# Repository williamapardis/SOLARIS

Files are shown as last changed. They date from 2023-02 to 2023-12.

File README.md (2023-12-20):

# SOLARIS
The Submersible Oceanic Luminescent Analyzer of Reactive Intermediate Species (SOLARIS) is a developmental instrument designed to make measurements in the ocean of a fleetingly scarce compound called superoxide(O<sup>2-</sup>), a reactive oxygen species(ROS) and made the first measurements of this chemical in the deep sea. SOLARIS utilizes the properties of chemiluminescence, a chemical reaction that produces light. Analysis involves mixing a chemical reagent with the seawater to be analyzed, after which a reaction occurs and produces light proportional to the level of superoxide. Measuring this light with a highly sensitive optical detector, a photon counting photomultiplier tube(PMT), we can very precisely determine how much superoxide is in the environment. Peristaltic pumps dispense reagents and seawater, which are encased in housings filled with (incompressible) oil to protect them from the corrosive environment. Electronics are encased in hermetically sealed pressure vessels held at atmospheric pressure  to protect them from both the seawater and hydrostatic pressure, allowing operation to depths of up to 4500 meters, corresponding to pressures of greater than 400 atmospheres.
SOALRIS has also been adapted to measure hydrogen peroxide (H<sub>2</sub>O<sub>2</sub>) and made some of the first ever measurments of this ROS species in the deep sea.
<div class="center">
  <table>
    <tr>
      <td>SOLARIS Pressure Testing</td>
       <td>System Schematic</td>
    </tr>
    <tr>
      <td></td>
      <td></td>
    </tr>
  </table>
</div>
  
## Hardware
SOLARIS is a complex assembly of mechanical electrical and fluidic components.

### Mechanical
The mechanical assembly of SOLARIS is broken into two sub-assemblies we reffer to as the Analyzer Assembly and the Reagent Assembly. 

#### Analyzer Assembly
The analyzer assembly is designed to be minipulated by a under water vehicle to be positioned near the area of interest to be analyzed.
<table>
  <tr>
    <td>Drawing</td>
    <td>On Deck</td>
    <td>In Water</td>
  </tr>
  <tr>
    <td></td>
    <td></td>
    <td></td>
  </tr>
</table>
<table>
  <tr>
    <td>Flow Cell</td>
  </tr>
  <tr>
    <td></td>
    <td>The Seawater sample and the chemiluminecent reagent (MCLA for measurement of O<sup>2-</sup>) enter the center of the spiral flow cell from their respective ports. This cell is optically monitoured through a optically clear saphire window by the PMT. Mixed fluids outflow the bottom port and are exhausted.</td>
  </tr>
</table>

#### Reagent Assembly
<table>
  <tr>
    <td>Drawning</td>
    <td>Diagram</td>
    <td>Image</td>
  </tr>
  <tr>
    <td></td>
    <td></td>
    <td>The Reagent assembly</td>
  </tr>
</table>

### Electrical
SOLARIS ELECTRICAL OVERVIEW:
- Pumps are driven by 7 Allmotion motor controllers.
- Allmotion motor controllers are controlled by custon WHOI PCB 23-0001-01.  Power to them is directly from instrument input.
- WHOI PCB 23-0001-01 contains Adafruit ItsyBitsy M4 which controlls the motor drivers over serial and manages overall device comminicaiton.  This board also prives power and communication to the PMT.
- COTS temperature controller (Wavelength Electronics) controlls SOTS chamber temperature.
- All data is stored onbaord the "topside" computer (none onboard Solaris itself).

#### Main Electrical Housing (Reagent Assembly)
<table>
  <tr>
    <td>Electronics Chassis</td>
    <td>Electronics Chassis Side</td>
    <td>Electronics Chassis Bottom</td>
  </tr>
  <tr>
    <td></td>
    <td></td>
    <td></td>
  </tr>
</table>

#### PMT Electrical Housing (Analyzer Assembly)
<table>
  <tr>
    <td>Full View PCB</td>
     <td>Zoomed View</td>
  </tr>
  <tr>
    <td></td>
    <td></td>
  </tr>
</table>

#### 23-0001-01 Custom Printed Circuit Board
<table>
  <tr>
    <td>Front PCB</td>
     <td>Bottom PCB</td>
  </tr>
  <tr>
    <td></td>
    <td></td>
  </tr>
</table>

#### Motors Controllers
The 7 pumps on SOLARIS are driven by motors and controled with [All Motion](https://www.allmotion.com/) [EZ10EN stepper motor driver](https://www.allmotion.com/ez10en). The 7 motor controllers share a parallel RS485 serial bus and are comunicated with a serial port on the 23-0001 controller through a [RS323 to RS485 converter](https://www.allmotion.com/rs485-ne).

#### Temperature Controller
The SOTs temperature control uses a Wavelength Electronics [RHM5K-CH termprature controller](https://www.teamwavelength.com/product/rhm5k-ch-5-a-unipolar-chassis-mt-temp-controller/) in combination with a resistive heater and thermistor. In order to maintain temperature stability we decided to remove the the integration capacitor.

#### Cables
[tubing](https://www.mcmaster.com/5549K55/) used with [MCPBOF](https://www.macartney.com/what-we-offer/systems-and-products/connectors/subconn/subconn-micro-circular-series/subconn-micro-circular-2-3-4-5-6-and-8-contacts-and-g2-2-3-and-4-contacts/)

### Fluid Handling

#### Pump Heads
<table>
  <tr>
    <td>Pump Head</td>
  </tr>
  <tr>
    <td></td>
    <td>The [100CPT parastaltic pump heads](https://www.wmcpumps.com/100cpt-series-micro-peristaltic-pump) were purchased from Williamson Manufacturing Company and used with the [100 Series Tube Sets](https://www.wmcpumps.com/100200220-series-tube-sets).</td>
  </tr>
</table>

#### Motors
These pumpheads are driven with the [HT11-021-G022 motor/gearbox](https://github.com/williamapardis/SOLARIS/blob/main/hardware/electrical/datasheets/Motor/HT11_021_GXXX_RevA_GEARMOTOR_ASSY-3079755.pdf) combo from Applied Motion Products. The output of the gearbox is coupled to the pump head with a custom machined shaft.



#### [tubing](https://www.mcmaster.com/5384K515/)

## Software
SOFTWARE OVERVIEW:
- There is a Matlab GUI that runs SOLARIS.  The GUI mostly updates pump speeds and and plots and stores data.
- There is firmware on the ItsyBitsy that sets the initial PMT and motor controller settings.  It also transmits data from the PMT to the topside computer, and it transmits speeds from the topside computer to the motor controllers. 

### The Application

#### Start up page


#### Real-Time GUI


#### Autonomous Mission Planning

### Using the Emulator

Download & install the free serial port emulator (emulator\free-virtual-serial-port-tools.exe)
  Select creat local bridge & configure:
    First port name: COM1
    Secound port name: COM2
  Create - select "Creat non-permanent device" checkbox and then OK
Run the emulator
  '''python3 emulator.py'''
Select previous datafile using explorer
Open the app and use on COM2

#### Dependencies
'''pip3 install scipy'''

### Firmware

#### 23_0001_01_Rb

#### Passthrough

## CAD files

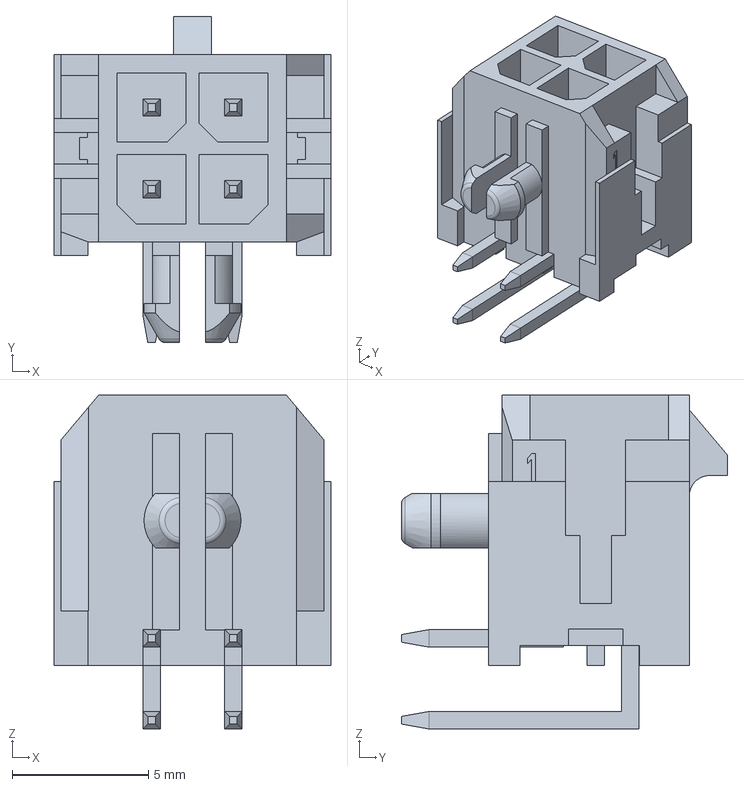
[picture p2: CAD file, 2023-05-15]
hardware/electrical/PCBs/23-0001/imported/3d/2_2 molex.stp
10.2 x 11.9 x 12.2 mm

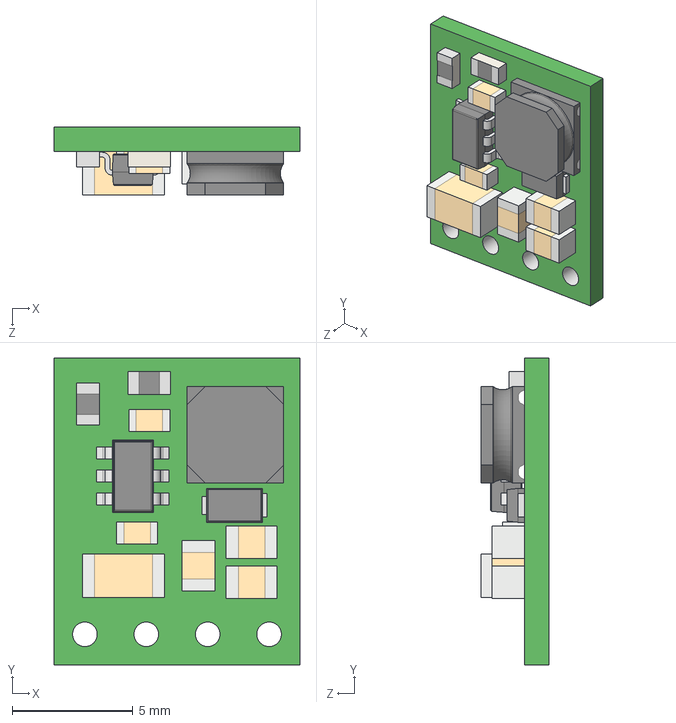
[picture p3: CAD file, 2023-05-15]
hardware/electrical/PCBs/23-0001/imported/3d/step-down-voltage-regulator-d24v3fx-d24v6fx-d36v6fx.step
10.2 x 12.7 x 2.82 mm

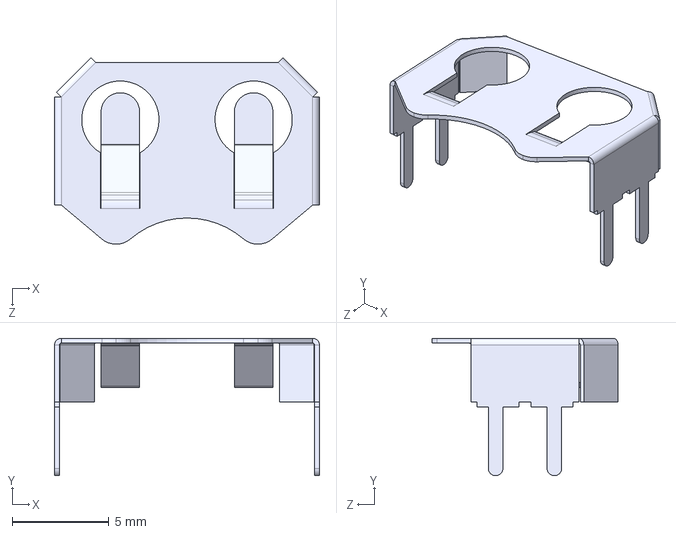
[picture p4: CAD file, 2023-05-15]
hardware/electrical/PCBs/23-0001/imported/3d/BK-917.STEP
13.7 x 7.11 x 9.65 mm

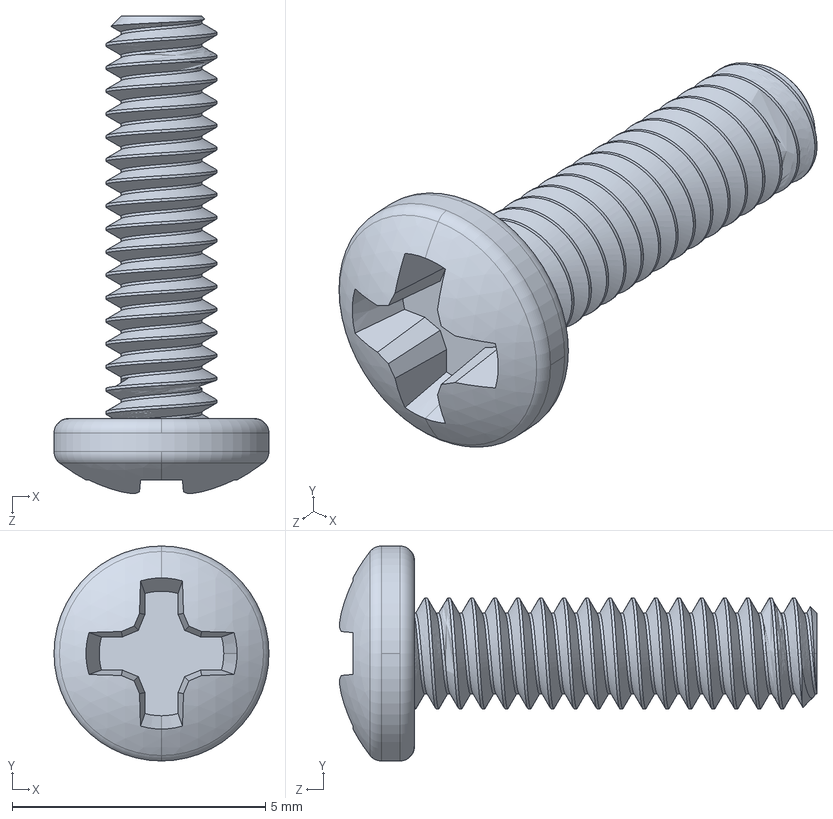
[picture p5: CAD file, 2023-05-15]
hardware/electrical/PCBs/23-0001/imported/3d/91400A056_MIL SPEC PAN HEAD PHILLIPS MACHINE SCREW.STEP
4.24 x 4.24 x 9.42 mm

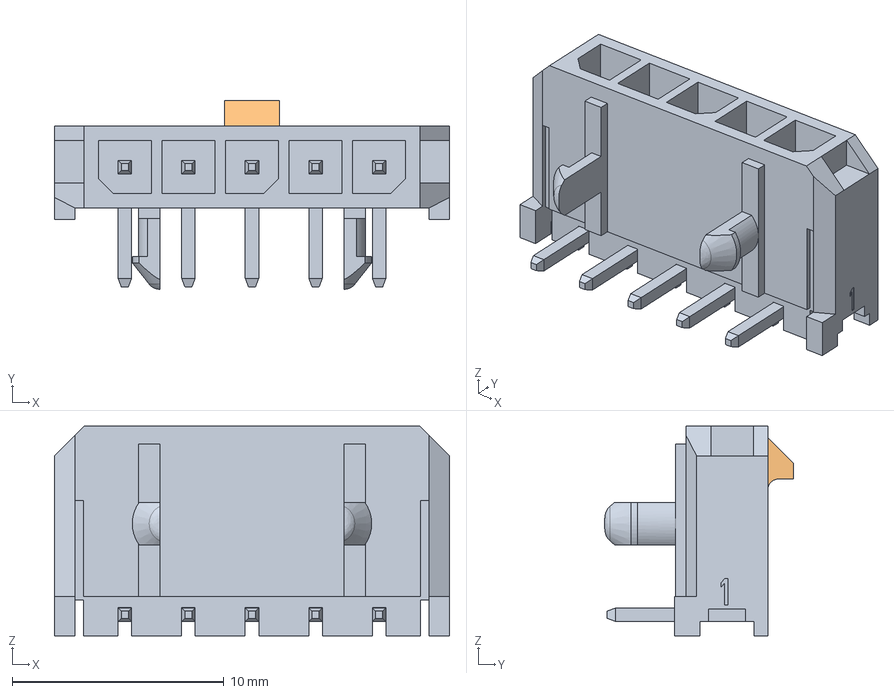
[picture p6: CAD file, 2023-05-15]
hardware/electrical/PCBs/23-0001/imported/3d/436500500.stp
18.6 x 8.91 x 9.90 mm

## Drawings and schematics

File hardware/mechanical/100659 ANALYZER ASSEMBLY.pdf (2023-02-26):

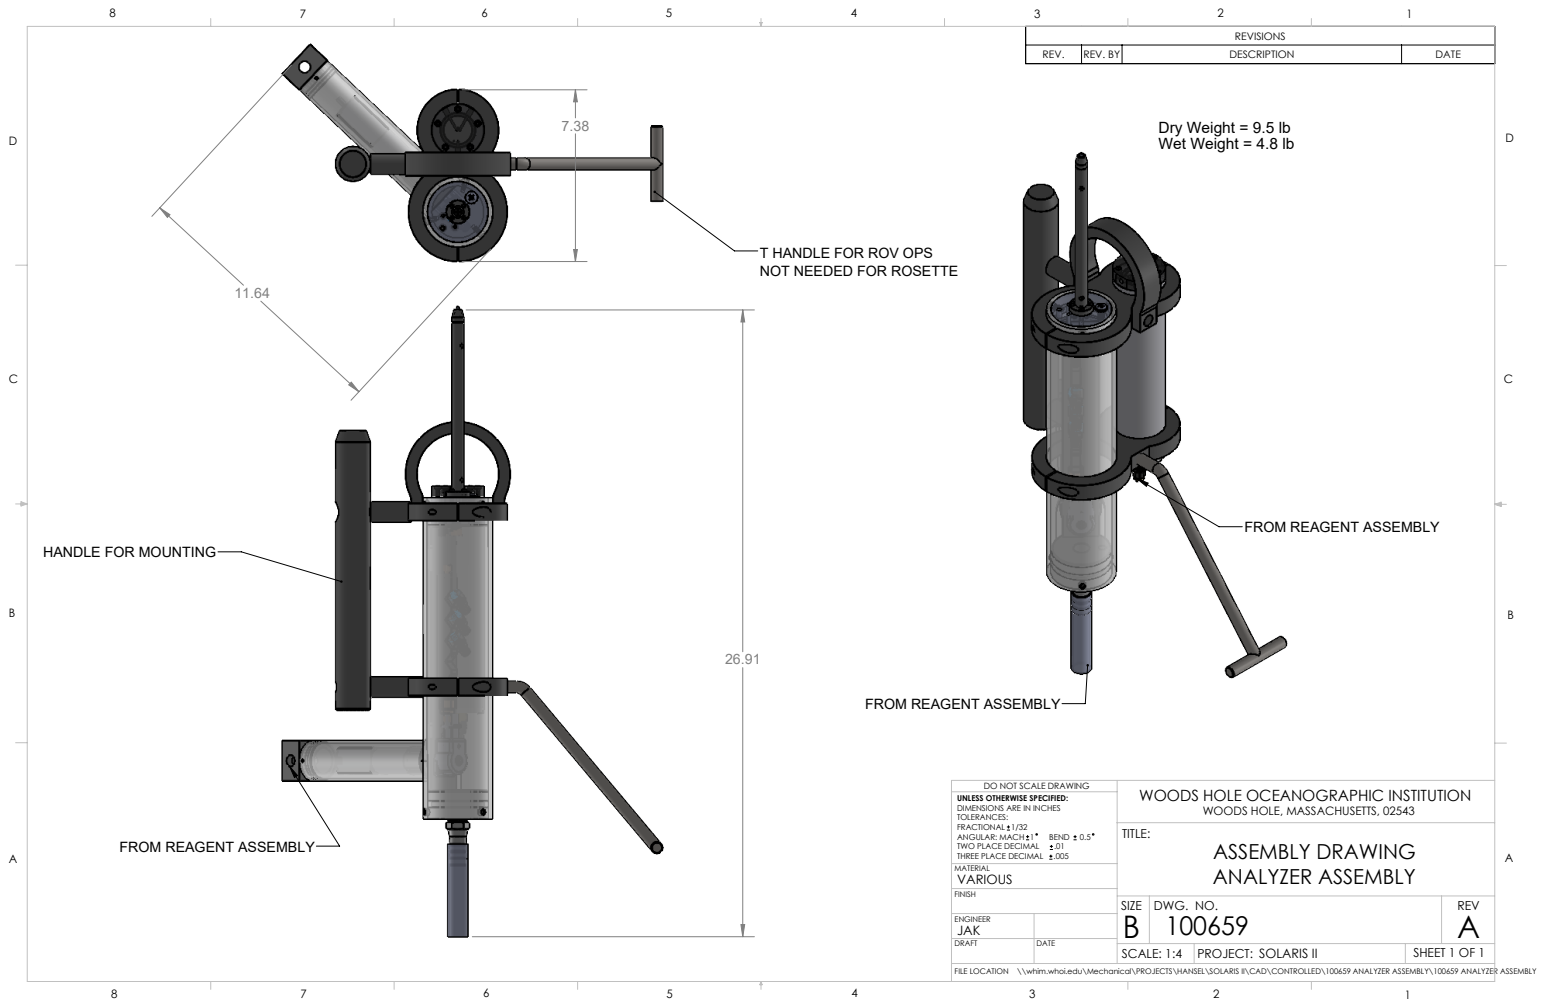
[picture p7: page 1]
REV.; REV. BY; DESCRIPTION; DATE; ANGULAR: MACH 1; BEND 0.5; TWO PLACE DECIMAL; DWG. NO.; REV; SHEET 1 OF 1; SCALE: 1:4; B ENGINEER; VARIOUS; ANALYZER ASSEMBLY

Dry Weight = 9.5 lb
Wet Weight = 4.8 lb

T HANDLE FOR ROV OPS
NOT NEEDED FOR ROSETTE

FROM REAGENT ASSEMBLY

HANDLE FOR MOUNTING

DO NOT SCALE DRAWING
UNLESS OTHERWISE SPECIFIED:
DIMENSIONS ARE IN INCHES
TOLERANCES:
FRACTIONAL 1/32
THREE PLACE DECIMAL .005
MATERIAL

WOODS HOLE OCEANOGRAPHIC INSTITUTION
ASSEMBLY DRAWING

WOODS HOLE, MASSACHUSETTS, 02543

PROJECT: SOLARIS II

FILE LOCATION \\whim.whoi.edu\Mechanical\PROJECTS\HANSEL\SOLARIS II\CAD\CONTROLLED\100659 ANALYZER ASSEMBLY\100659 ANALYZER ASSEMBLY

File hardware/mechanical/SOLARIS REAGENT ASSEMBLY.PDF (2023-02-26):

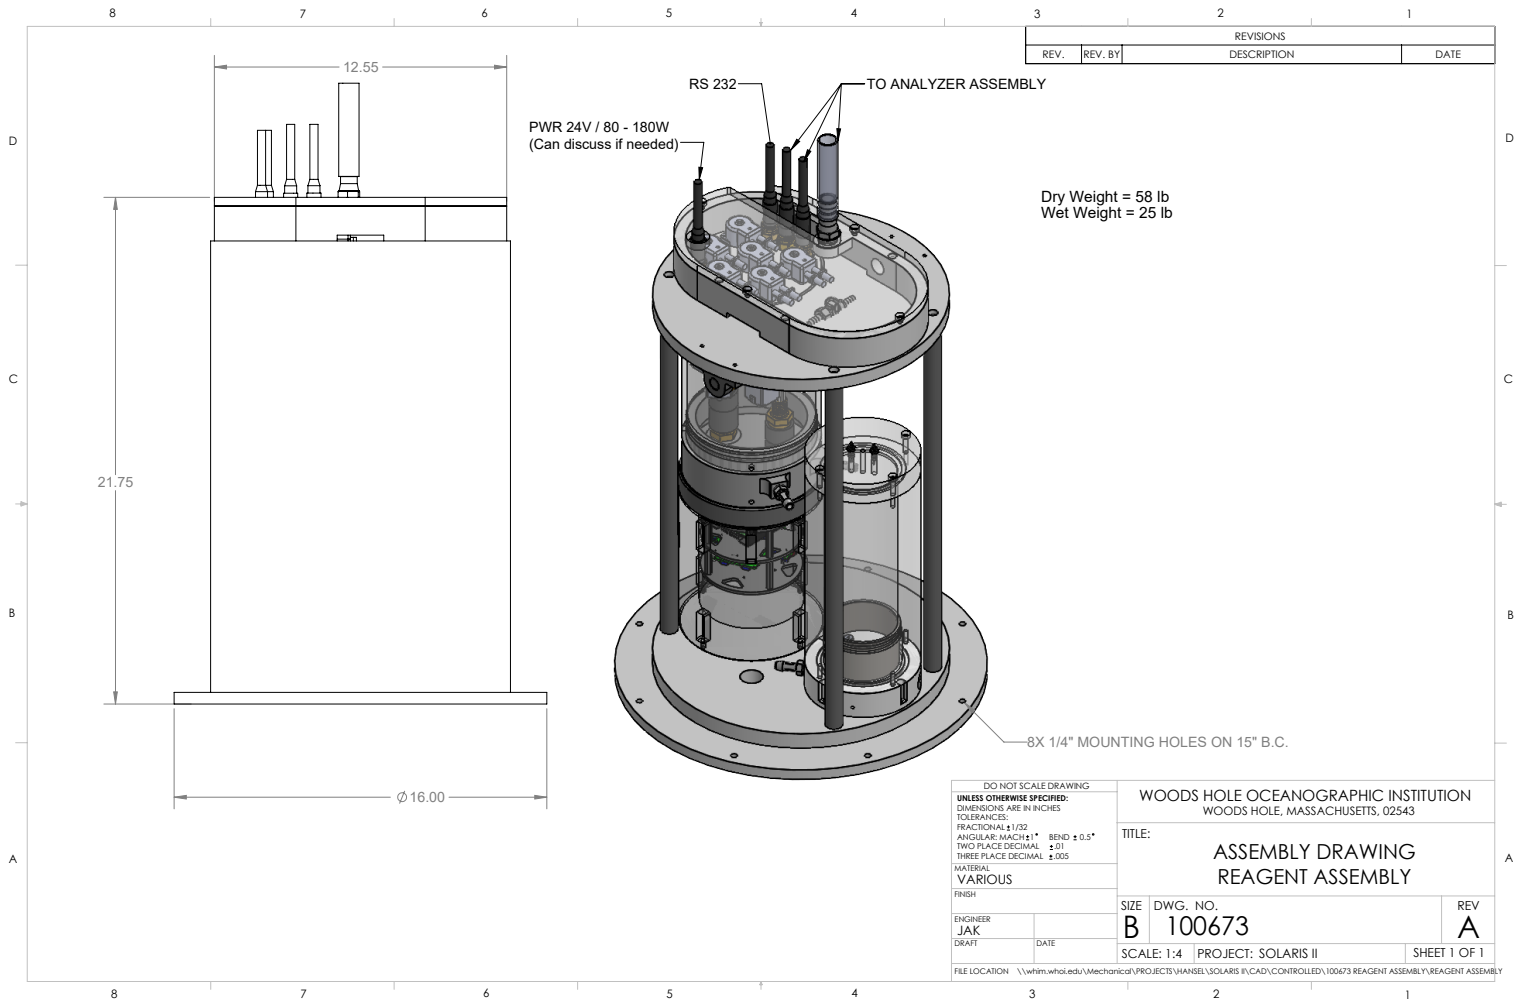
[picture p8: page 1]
REV.; REV. BY; DESCRIPTION; DATE; ANGULAR: MACH 1; BEND 0.5; TWO PLACE DECIMAL; DWG. NO.; REV; SHEET 1 OF 1; SCALE: 1:4; B ENGINEER; VARIOUS; REAGENT ASSEMBLY

TO ANALYZER ASSEMBLY

PWR 24V / 80 - 180W
(Can discuss if needed)

Dry Weight = 58 lb
Wet Weight = 25 lb

8X 1/4" MOUNTING HOLES ON 15" B.C.

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

WOODS HOLE OCEANOGRAPHIC INSTITUTION
ASSEMBLY DRAWING

WOODS HOLE, MASSACHUSETTS, 02543

PROJECT: SOLARIS II

FILE LOCATION \\whim.whoi.edu\Mechanical\PROJECTS\HANSEL\SOLARIS II\CAD\CONTROLLED\100673 REAGENT ASSEMBLY\REAGENT ASSEMBLY

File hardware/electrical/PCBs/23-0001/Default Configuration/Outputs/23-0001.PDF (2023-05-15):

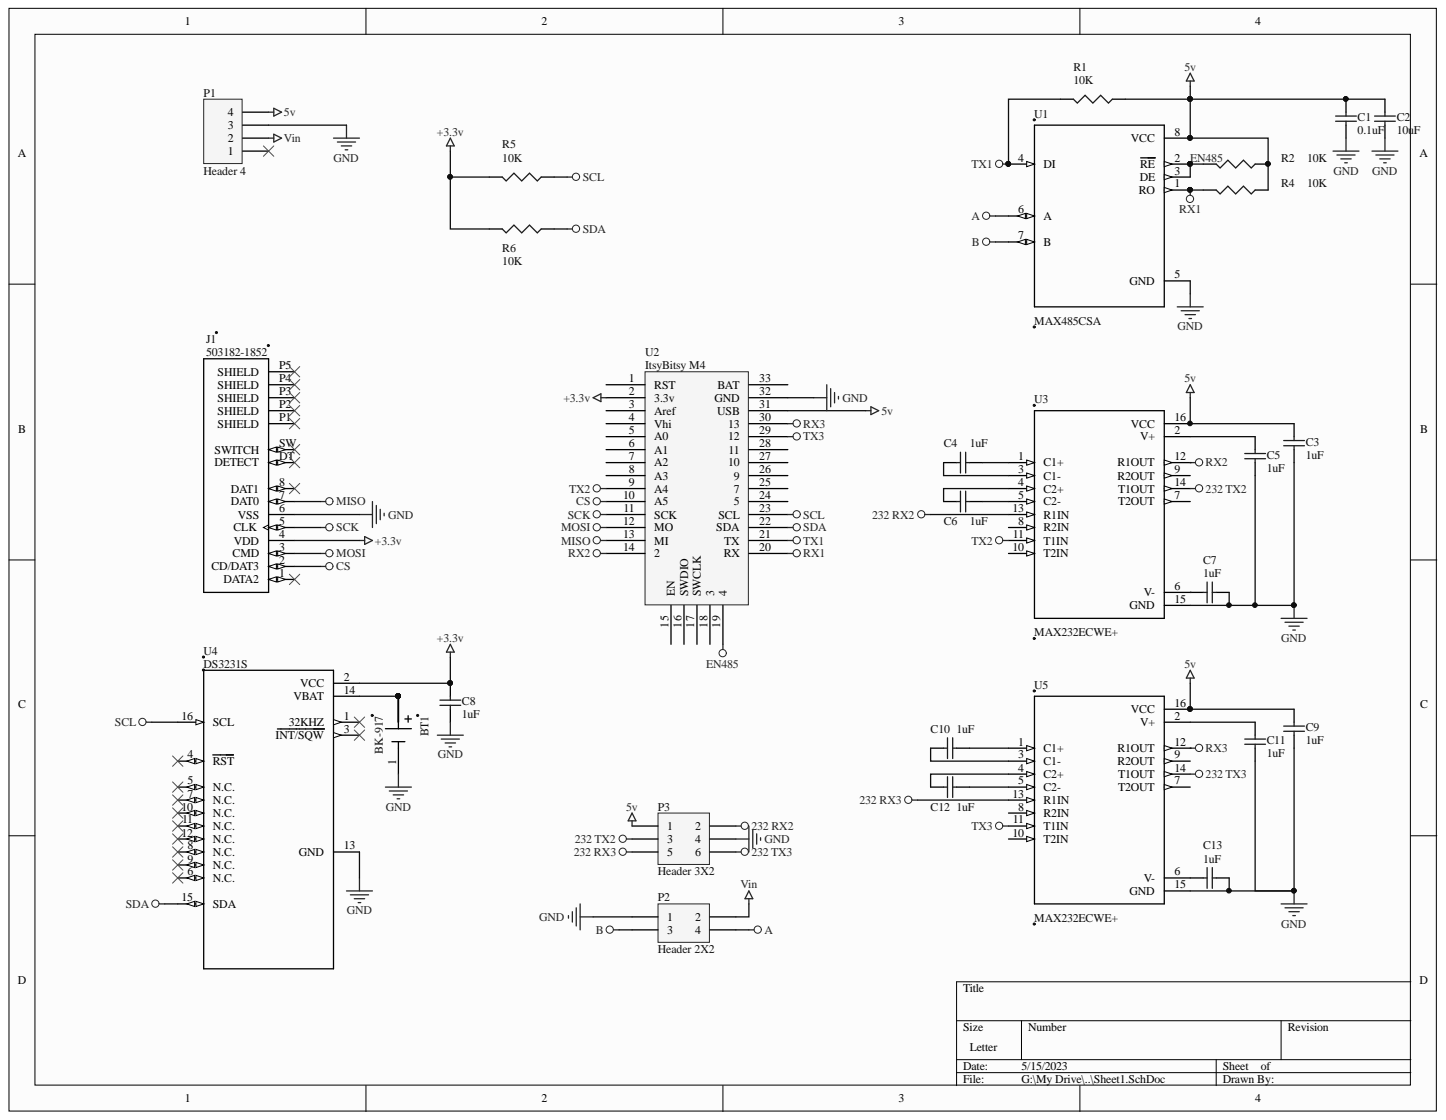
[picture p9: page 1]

4 19 RX 20 TX 21 SDA 22 SCL 23 5 24 7 25 9 26 10 27 11 28 12 29 13 30 USB 31 GND 32 BAT 33

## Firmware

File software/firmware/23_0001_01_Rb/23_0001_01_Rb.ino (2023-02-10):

//Libraries
#include <Arduino.h>          // required before wiring_private.h
#include "wiring_private.h"   // pinPeripheral() function
#include "RTClib.h"           // for ds3231 clock
#include <SPI.h>
#include <SD.h>

////////////SERCOM SETUP////////////////////////////////////////////////////////////////
//SERCOM PIN and PAD assigment for serial2 (PMT)
#define PIN_SERIAL2_RX 2   //D2
#define PAD_SERIAL2_RX (SERCOM_RX_PAD_3)
#define PIN_SERIAL2_TX 18  //A4
#define PAD_SERIAL2_TX (UART_TX_PAD_0)
Uart Serial2( &sercom0, PIN_SERIAL2_RX, PIN_SERIAL2_TX, PAD_SERIAL2_RX, PAD_SERIAL2_TX );

//SERCOM PIN and PAD assigment for serial3 (user interface)
#define PIN_SERIAL3_RX 13  //D13
#define PAD_SERIAL3_RX (SERCOM_RX_PAD_1)
#define PIN_SERIAL3_TX 12  //D12
#define PAD_SERIAL3_TX (UART_TX_PAD_0)
Uart Serial3( &sercom5, PIN_SERIAL3_RX, PIN_SERIAL3_TX, PAD_SERIAL3_RX, PAD_SERIAL3_TX); // 13(D13 =>PA22 => Sercom 5.1) , 12(D12 =>PA23 => Sercom 5.0)

Stream *SERIALOUT = &Serial2;

void SERCOM0_0_Handler() {
  Serial2.IrqHandler();
}
void SERCOM0_1_Handler() {
  Serial2.IrqHandler();
}
void SERCOM0_2_Handler() {
  Serial2.IrqHandler();
}
void SERCOM0_3_Handler() {
  Serial2.IrqHandler();
}

void SERCOM5_0_Handler() {
  Serial3.IrqHandler();
}
void SERCOM5_1_Handler() {
  Serial3.IrqHandler();
}
void SERCOM5_2_Handler() {
  Serial3.IrqHandler();
}
void SERCOM5_3_Handler() {
  Serial3.IrqHandler();
}

////////////PIN DEFINITIONS////////////////////////////////////////////////////////////////
const int chipSelect = A5;  //select pin for SD card
const int EN485 = 4;        //RS485 (pump coms) enable. high=TX, low=RX
const int rst   = 3;

const int BUFsize = 10;
//File name for datalog file
String logFN = "";
bool armed = true;

RTC_DS3231 rtc;

int Twait=0,Tstar=0,Tnow=0;
int CC=1;

void setup() {

  //enable RS485 as transmit
  pinMode(EN485, OUTPUT); digitalWrite(EN485, HIGH);
  pinMode(rst,OUTPUT);digitalWrite(rst,HIGH);

  //setting ADC resolution
  analogReadResolution(12);
  
  //begin USB, RS458/pump, RS232/PMT, and RS232/user interface at 9600 bruad
  Serial.begin(9600); Serial1.begin(9600); Serial2.begin(9600); Serial3.begin(9600);

  //SERCOM
  pinPeripheral(PIN_SERIAL2_RX, PIO_SERCOM_ALT);
  pinPeripheral(PIN_SERIAL2_TX, PIO_SERCOM_ALT);
  pinPeripheral(PIN_SERIAL3_RX, PIO_SERCOM_ALT);
  pinPeripheral(PIN_SERIAL3_TX, PIO_SERCOM_ALT);
  
  PRINT("initializing SD... ");
  if (!SD.begin(chipSelect)) {
    Serial.println("Card failed, or not present");
  }
  PRINT("SD initialized\n");

  sendMotorCom("/_TR");

  int Tstart = 180000; //delay time in ms before start
  int timer = millis();
  
  while (millis() < Tstart) {

    delay(1000);

    if (millis() - timer > 5000) {
      timer = millis();
      if (armed) {
        PRINT("\nsystem is armed\n");
      }
      else {
        PRINT("\nsystem is not armed\n");
      }

      PRINT("starting in: ");
      PRINT(String((Tstart - millis()) / 1000));
      PRINT(" [sec]");

    }

    char Abuf[BUFsize];
    memset(Abuf, 0, sizeof Abuf);
    comCheck(Abuf,BUFsize);
    if (String(Abuf) == "disarm") {
      PRINT("\nSYSTEM DISARMED\n");
      armed = false;
      sendMotorCom("/4J0R");
      break;
    }
    else if(String(Abuf) == "upload"){

      Tstart=Tstart-millis();
      
      char fBuf[100];
      PRINT("\n");

      PRINT("current mission.txt will be deleted\n");
      PRINT("Sure you want to upload (Y/N): ");
      while(Serial.available()==0 && Serial3.available()==0){}
      comCheck(fBuf,100);
      PRINT(String(fBuf));PRINT("\n");

      if(String(fBuf)=="Y"){
        SD.remove("mission.txt");
      }
      else{
        digitalWrite(rst,LOW);
      }
      
      while(true){
      memset(fBuf, 0, sizeof fBuf);
        PRINT("input line: ");
        while(Serial.available()==0 && Serial3.available()==0){}
        comCheck(fBuf,100);     
        printLineToFile(String(fBuf),"mission.txt");
        PRINT(fBuf);PRINT("\n");
        if(String(fBuf)=="done"){
          break;
        }
      }
      Tstart=Tstart+millis();
    }
    else if(String(Abuf) == "reset"){
      Serial.println("RESETING");
      digitalWrite(rst,LOW);
    }
    else if(String(Abuf) == "skip"){
      break;
    }

    PRINT(".");

  }

  PRINT("initializing RTC... ");
  if (!rtc.begin()) {
    PRINT("Couldn't find RTC\n");
  }
  PRINT("RTC initialized\n");
//  if (rtc.lostPower()) {
//    PRINT("RTC lost power\n");
//    // following line sets the RTC to the date & time this sketch was compiled
//    rtc.adjust(DateTime(F(__DATE__), F(__TIME__)));
//    // This line sets the RTC with an explicit date & time, for example to set
//    // January 21, 2014 at 3am you would call:
//    // rtc.adjust(DateTime(2014, 1, 21, 3, 0, 0));
//  }

  PRINT("setting filename... ");
  setFilename();
  PRINT("filename set to: "); PRINT(logFN); PRINT("\n");

  if (armed){
    PRINT("Printing file\n");
    printFile("mission.txt");
    DateTime now = rtc.now();
    Tstar=now.unixtime();
    Twait=sendMissionCommand(CC);
//    PRINT("next action in: ");PRINT(String(Twait));PRINT(" seconds\n");
//    PRINT("Starting from: ");PRINT(String(Tstar));PRINT(" unixtime\n");
    CC++;
  }


  //PMT initilization settings
  PRINT("setting up PMT...");
  Serial2.write("P1\r");  //integration time
  while (Serial2.available()) {
    Serial2.read();
  }
  Serial2.write("D\r");   //votage
  while (Serial2.available()) {
    Serial2.read();
  }
  Serial2.write("C\r");   //start continuous read
  PRINT("PMT initialized\n");
  delay(100);



}


bool MCF = false; //motor command flag
char buf[BUFsize], mybuf[4];
int PS1 = 0, PS2 = 0, PS3 = 0, PS4 = 0, PS5 = 0, PS6 = 0, PS7 = 0; //pump state: 1 on, 0 off
int PF1 = 2440, PF2 = 2440, PF3 = 2440, PF4 = 2440, PF5 = 2440, PF6 = 2440, PF7 = 2440; //pump flow: 0 to 160000

void loop() {

  if(armed){
  DateTime now = rtc.now();
  Tnow=now.unixtime();
    if(Tnow>=Tstar+Twait){
      Tstar=now.unixtime();
      Twait=sendMissionCommand(CC);
      CC++;
  //    PRINT("next action in: ");PRINT(String(Twait/1000));PRINT(" seconds\n");
  //    PRINT("Starting from: ");PRINT(String(Tstar));PRINT(" unixtime\n");
    }
  }
  
  memset(buf, 0, sizeof buf);   //empty char array buffer
  //delay(5);
  
  if (Serial3.available() > 0) {

    Serial3.readBytesUntil('|', buf, 10);
    Serial.print("BUFF: ");Serial.println(sizeof(buf));
    
    if (buf[0] == '/') {
      sendMotorCom(buf);
      Serial.print("Sending (1): ");
    }
    else if(String(buf) == "reset"){
      Serial.println("RESETING");
      digitalWrite(rst,LOW);
    }
//    else {
//      Serial.println(buf);
//      Serial2.print(buf);
//      Serial.print("Sending (2): ");
//    }
    Serial.println(buf);
  }

  dataAquire();


  
  while(Serial1.available()>0){
    Serial.print("MOTOR AVAILABLE: ");Serial.println(Serial1.available());
    Serial.write(Serial1.read());
  }

}

void dataAquire(){
  
  if (Serial2.available() > 0) {
    String data = "";
    data += isoTime();
    data += ',';
    delay(5);
    while (Serial2.available() > 0) {  // If anything comes in Serial1 (pins 0 & 1)
      Serial2.readBytes(mybuf, 4);
    }
    data += (uint32_t)mybuf[0] << 24 | (uint32_t)mybuf[1] << 16 | (uint32_t)mybuf[2] << 8 | (uint32_t)mybuf[3];
    //analog channels
    data += ',';data+=(float(analogRead(A0))/4095)*3.3;//Actual Temp
    //data += ',';data+=analogRead(A1);//Set Temp
    //data += ',';data+=analogRead(A2);//Limit
    //if pump on record velocity, if not state 0
    data += ','; if (PS1) {
      data += PF1;
    } else {
      data += '0';
    };
    data += ','; if (PS2) {
      data += PF2;
    } else {
      data += '0';
    };
    data += ','; if (PS3) {
      data += PF3;
    } else {
      data += '0';
    };
    data += ','; if (PS4) {
      data += PF4;
    } else {
      data += '0';
    };
    data += ','; if (PS5) {
      data += PF5;
    } else {
      data += '0';
    };
    data += ','; if (PS6) {
      data += PF6;
    } else {
      data += '0';
    };
    data += ','; if (PS7) {
      data += PF7;
    } else {
      data += '0';
    };
    Serial.print("Recieved (2): ");
    PRINT(data); PRINT("\n");
    printLineToFile(data,logFN);
  }
  
}

char * comCheck(char BUF[],int howBig) {

  memset(BUF, 0, sizeof BUF);   //empty char array buffer
  delay(5);

  if (Serial.available() > 0) {
    Serial.readBytesUntil('\r', BUF, howBig);
  }
  else if (Serial3.available() > 0) {
    Serial3.readBytesUntil('\r', BUF, howBig);
  }

  return BUF;

}



void PRINT(String text) {
  Serial.print(text);
  Serial3.print(text);
}



//returns iso formated time
String isoTime() {

  DateTime now = rtc.now();

  String t = "";

  t += String(now.year(), DEC);
  if (now.month() < 10) {
    t += '0';
  }
  t += String(now.month(), DEC);
  if (now.day() < 10) {
    t += '0';
  }
  t += String(now.day(), DEC);
  t += "T";
  if (now.hour() < 10) {
    t += '0';
  }
  t += String(now.hour(), DEC);
  if (now.minute() < 10) {
    t += '0';
  }
  t += String(now.minute(), DEC);
  if (now.second() < 10) {
    t += '0';
  }
  t += String(now.second(), DEC);

  return t;

}

void sendMotorCom(char buff[]){
  Serial1.println(buff);
  checkPumpChange(buff);
}

void checkPumpChange(char buff[10]) {

  if (buff[2] == 'P') {
    switch (buff[1]) {
      case '1':
        PS1 = 1;
        break;
      case '2':
        PS2 = 1;
        break;
      case '3':
        PS3 = 1;
        break;
      case '4':
        PS4 = 1;
        break;
      case '5':
        PS5 = 1;
        break;
      case '6':
        PS6 = 1;
        break;
      case '7':
        PS7 = 1;
        break;
    }
  }
  else if (buff[2] == 'T') {
    switch (buff[1]) {
      case '1':
        PS1 = 0;
        break;
      case '2':
        PS2 = 0;
        break;
      case '3':
        PS3 = 0;
        break;
      case '4':
        PS4 = 0;
        break;
      case '5':
        PS5 = 0;
        break;
      case '6':
        PS6 = 0;
        break;
      case '7':
        PS7 = 0;
        break;
    }
  }
  else if (buff[2] == 'V') {
    switch (buff[1]) {
      case '1':
        PF1 = atoi(&buff[3]);
        break;
      case '2':
        PF2 = atoi(&buff[3]);
        break;
      case '3':
        PF3 = atoi(&buff[3]);
        break;
      case '4':
        PF4 = atoi(&buff[3]);
        break;
      case '5':
        PF5 = atoi(&buff[3]);
        break;
      case '6':
        PF6 = atoi(&buff[3]);
        break;
      case '7':
        PF7 = atoi(&buff[3]);
        break;
    }
  }

}

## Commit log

2023-02-13 added temperature sensing
2023-02-26 motor invoice
2023-02-26 anaylzer and reagent assembly drawings
2023-02-28 temperature contoller data
2023-04-17 swapping pump associations
2023-04-18 fixed Matlab timezone to UTZ. Quick pump association change before the dive.
2023-04-19 re-integrated auto calibrate feature
2023-04-22 probably just the SOTs pump re-association
2023-04-22 datafile now stores flowrate
2023-05-03 motor datasheet
2023-05-04 flow rate change FKt20230504
2023-05-15 PCB files
    [23-0001.PrjPcb, 2_2 molex.stp, 2_3 molex.stp, 436500500.stp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]
